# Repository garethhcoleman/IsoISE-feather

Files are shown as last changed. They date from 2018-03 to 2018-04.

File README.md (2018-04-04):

# IsoISE-feather
##Hardware files for IsoISE feather board

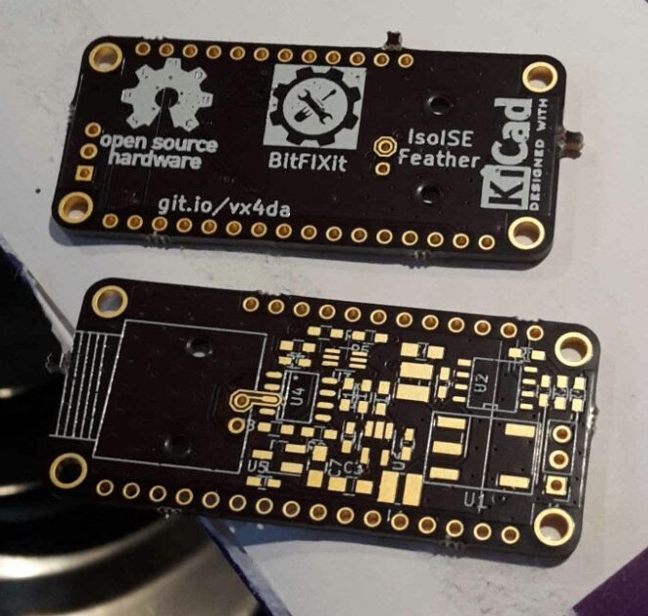
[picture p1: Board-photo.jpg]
Photo of IsoISE boards without components IsoISE boards without components

In this repo you will find all the design files; I hope it is everything you need to reproduce and hopefully improve my work.

This circuit is heavily based on wonderful work by Ryan Edwards at sparkyswidgets.com.

I emailed Ryan because I wanted to ask if he was happy for me to just make his isoion project, which is not strictly necessary but I think is good manners. He gave me his blessing to go ahead. I thought it was especially important to do this since he was selling his projects (although not this one, my orignal motivation for making it) and I wasn't then intending to modify his design. Subsequently I took the bull by the horns and dove into (partially!) understanding and modifying his designs, so I took his more advanced [ion selective electrode interface project](https://www.sparkyswidgets.com/portfolio-item/ion-selective-electrode-interface/) and went from there.

As you can see by comparing our circuits, I copied his design for the isolated I2C based ADC and digital pot, applied to a TL072 JFET op-amp front end. The only significant changes I made were to replace the isolated power supply and separate -5V generator with an isolated supply able to generate +-5V from 3.3V. I did this because the original ADUM6010 datasheet does not recommend the combination of VIN=3.3V and VOUT=5V.

The PCB layout is my own work, my first ever board produced and already I can see issues!! The guard rings around the signal input pin are very tightly spaced making soldering difficult - in a future revision I will increase the spacing there. I somehow ended up skipping the reference R3 - so there are 11 resistors on board numbered R1-R12. Again, I'll correct this in future revisions. I didn't pay much attention to silkscreen component references so assembly will require reference to the board layout in Kicad....

I'm following Dave Jones' OSHW logo and definition: https://www.eevblog.com/oshw/

S = Schematic - Included
P = PCB - Included
F = Firmware and/or software - TO BE DONE
M = Mechanical CAD files - NOT APPLICABLE
D = Design Documentation - This document
B = Bill Of Materials - Included
C = License used allows for commercial use - YES

I've used open software to produce these files: Kicad 4.0.7, LibreOffice 4.3 and Remarkable 1.87

You can order the revision 1 board at [OSH Park](https://oshpark.com/shared_projects/bHu0gW7W).
Additionally, a shared basket of almost all the required components is [available at digikey](http://www.digikey.co.uk/short/jpfbn8).

Licensed under the Creative Commons Attribution-ShareAlike 3.0 Unported license, following the license of the originating project.

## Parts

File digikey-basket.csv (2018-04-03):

Index | Quantity | Part Number | Description | Customer Reference | Available Quantity | Backorder Quantity | Unit Price GBP | Extended Price GBP
1 | 4 | 811-2374-ND | DC/DC CONVERT +/-5V 100MA 1W SMD | U1 | 4 | 0 | 5.39 | 21.56
2 | 4 | ADUM1250ARZ-ND | DGTL ISO 2.5KV 2CH I2C 8SOIC | U2 | 4 | 0 | 4.17 | 16.68
3 | 4 | MCP4017T-104E/LTCT-ND | IC DGTL POT 100K 128TAPS SC70-6 | U3 | 4 | 0 | 0.38 | 1.52
4 | 4 | 497-7040-1-ND | IC OPAMP JFET 4MHZ 8SO | U4 | 4 | 0 | 0.41 | 1.64
5 | 4 | 296-17098-1-ND | IC VREF SERIES 3V SOT23-3 | U5 | 4 | 0 | 1.93 | 7.72
6 | 4 | MCP3221A5T-I/OTCT-ND | IC ADC 12BIT 2.7V 1CH LP SOT23-5 | U6 | 4 | 0 | 1.05 | 4.2
7 | 20 | 399-15351-1-ND | CAP CER 0.1UF 6.3V X7R 0603 | C1,C2,C5,C6,C9 | 20 | 0 | 0.165 | 3.3
8 | 12 | 399-8014-1-ND | CAP CER 10UF 6.3V X5R 0805 | C3,C4,C7 | 12 | 0 | 0.126 | 1.51
9 | 4 | 399-15379-1-ND | CAP CER 220PF 10V X7R 0603 | C8 | 4 | 0 | 0.23 | 0.92
10 | 4 | ARF1065-ND | CONN BNC JACK R/A 50 OHM PCB | J2 | 4 | 0 | 2.82 | 11.28
11 | 8 | 811-2473-1-ND | FIXED IND 10UH 500MA 400 MOHM | L1,L2 | 8 | 0 | 0.23 | 1.84
12 | 12 | 541-4040-1-ND | RES SMD 3K OHM 1% 1/10W 0603 | R1,R2,R9 | 12 | 0 | 0.019 | 0.23
13 | 12 | 541-2201-1-ND | RES SMD 4.7K OHM 1% 1/10W 0603 | R4,R5,R6 | 12 | 0 | 0.056 | 0.67
14 | 4 | 311-10KDCT-ND | RES SMD 10K OHM 0.5% 1/10W 0603 | R7 | 4 | 0 | 0.08 | 0.32
15 | 8 | 311-2103-1-ND | RES SMD 100K OHM 0.5% 1/10W 0603 | R8,R10 | 8 | 0 | 0.11 | 0.88
16 | 4 | 311-1.0KDCT-ND | RES SMD 1K OHM 0.5% 1/10W 0603 | R11 | 4 | 0 | 0.08 | 0.32
17 | 4 | 311-499DCT-ND | RES SMD 499 OHM 0.5% 1/10W 0603 | R12 | 4 | 0 | 0.08 | 0.32

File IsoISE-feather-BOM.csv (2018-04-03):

Ref | Value | Part Ordered | Footprint | Datasheet
U1 | MTU1D0305MC | MTU1D0305MC | 5pinMTU | https://power.murata.com/data/power/ncl/kdc_mtu1.pdf
U2 | ADUM1250 | ADUM1250ARZ | SOIC-8-N | http://www.analog.com/media/en/technical-documentation/data-sheets/ADUM1250_1251.pdf
U3 | MCP4017 | MCP4017T-104E/LT | SOT-363_SC-70-6 | http://ww1.microchip.com/downloads/en/DeviceDoc/22147a.pdf
U4 | TL072 | TL072BIDT | SOP-8L | http://www.st.com/content/ccc/resource/technical/document/datasheet/bb/4d/19/24/7d/40/48/a6/CD00000490.pdf/files/CD00000490.pdf/jcr:content/translations/en.CD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
U5 | REF3130 | REF3130AIDBZT | SOT-23-3 | http://www.ti.com/lit/ds/symlink/ref3130.pdf
U6 | MCP3221 | MCP3221A5T-I/OT | SOT-23-5 | http://ww1.microchip.com/downloads/en/DeviceDoc/20001732E.pdf
C1 | 0.1uF | C0603C104K9RAC7867 | 603 | https://content.kemet.com/datasheets/KEM_C1002_X7R_SMD.pdf
C2 | 0.1uF | C0603C104K9RAC7867 | 603 | https://content.kemet.com/datasheets/KEM_C1002_X7R_SMD.pdf
C3 | 10uF | C0805C106M9PACTU | 805 | https://content.kemet.com/datasheets/KEM_C1002_X7R_SMD.pdf
C4 | 10uF | C0805C106M9PACTU | 805 | https://content.kemet.com/datasheets/KEM_C1002_X7R_SMD.pdf
C5 | 0.1uF | C0603C104K9RAC7867 | 603 | https://content.kemet.com/datasheets/KEM_C1002_X7R_SMD.pdf
C6 | 0.1uF | C0603C104K9RAC7867 | 603 | https://content.kemet.com/datasheets/KEM_C1002_X7R_SMD.pdf
C7 | 10uF | C0805C106M9PACTU | 805 | https://content.kemet.com/datasheets/KEM_C1002_X7R_SMD.pdf
C8 | 220pF | C0603C221K8RAC7867 | 603 | https://content.kemet.com/datasheets/KEM_C1002_X7R_SMD.pdf
C9 | 0.1uF | C0603C104K9RAC7867 | 603 | https://content.kemet.com/datasheets/KEM_C1002_X7R_SMD.pdf
J1 | Conn_01x03 | Standard pin header | 1x03_Pitch2.54mm
J2 | BNC | 31-5431 | BNC-Amphenol | https://www.amphenolrf.com/downloads/dl/file/id/7797/product/565/031_5431_10rfx_customer_drawing.pdf
J3 | FeatherWing | OshPARK
L1 | 10uH | 82103C | Murata_8200 | https://www.murata-ps.com/data/magnetics/kmp_8200c.pdf
L2 | 10uH | 82103C | Murata_8200 | https://www.murata-ps.com/data/magnetics/kmp_8200c.pdf
R1 | 3K | CRCW06033K00FKEAC | 603
R2 | 3K | CRCW06033K00FKEAC | 603
R4 | 4.7K | RCA06034K70FKEA | 603
R5 | 4.7K | RCA06034K70FKEA | 603
R6 | 4.7K | RCA06034K70FKEA | 603
R7 | 10K | RT0603DRD0710KL | 603
R8 | 100K | AT0603DRD07100KL | 603
R9 | 3K | CRCW06033K00FKEAC | 603
R10 | 100K | AT0603DRD07100KL | 603
R11 | 1K | RT0603DRD071KL | 603
R12 | 500R | RT0603DRD07499RL | 603

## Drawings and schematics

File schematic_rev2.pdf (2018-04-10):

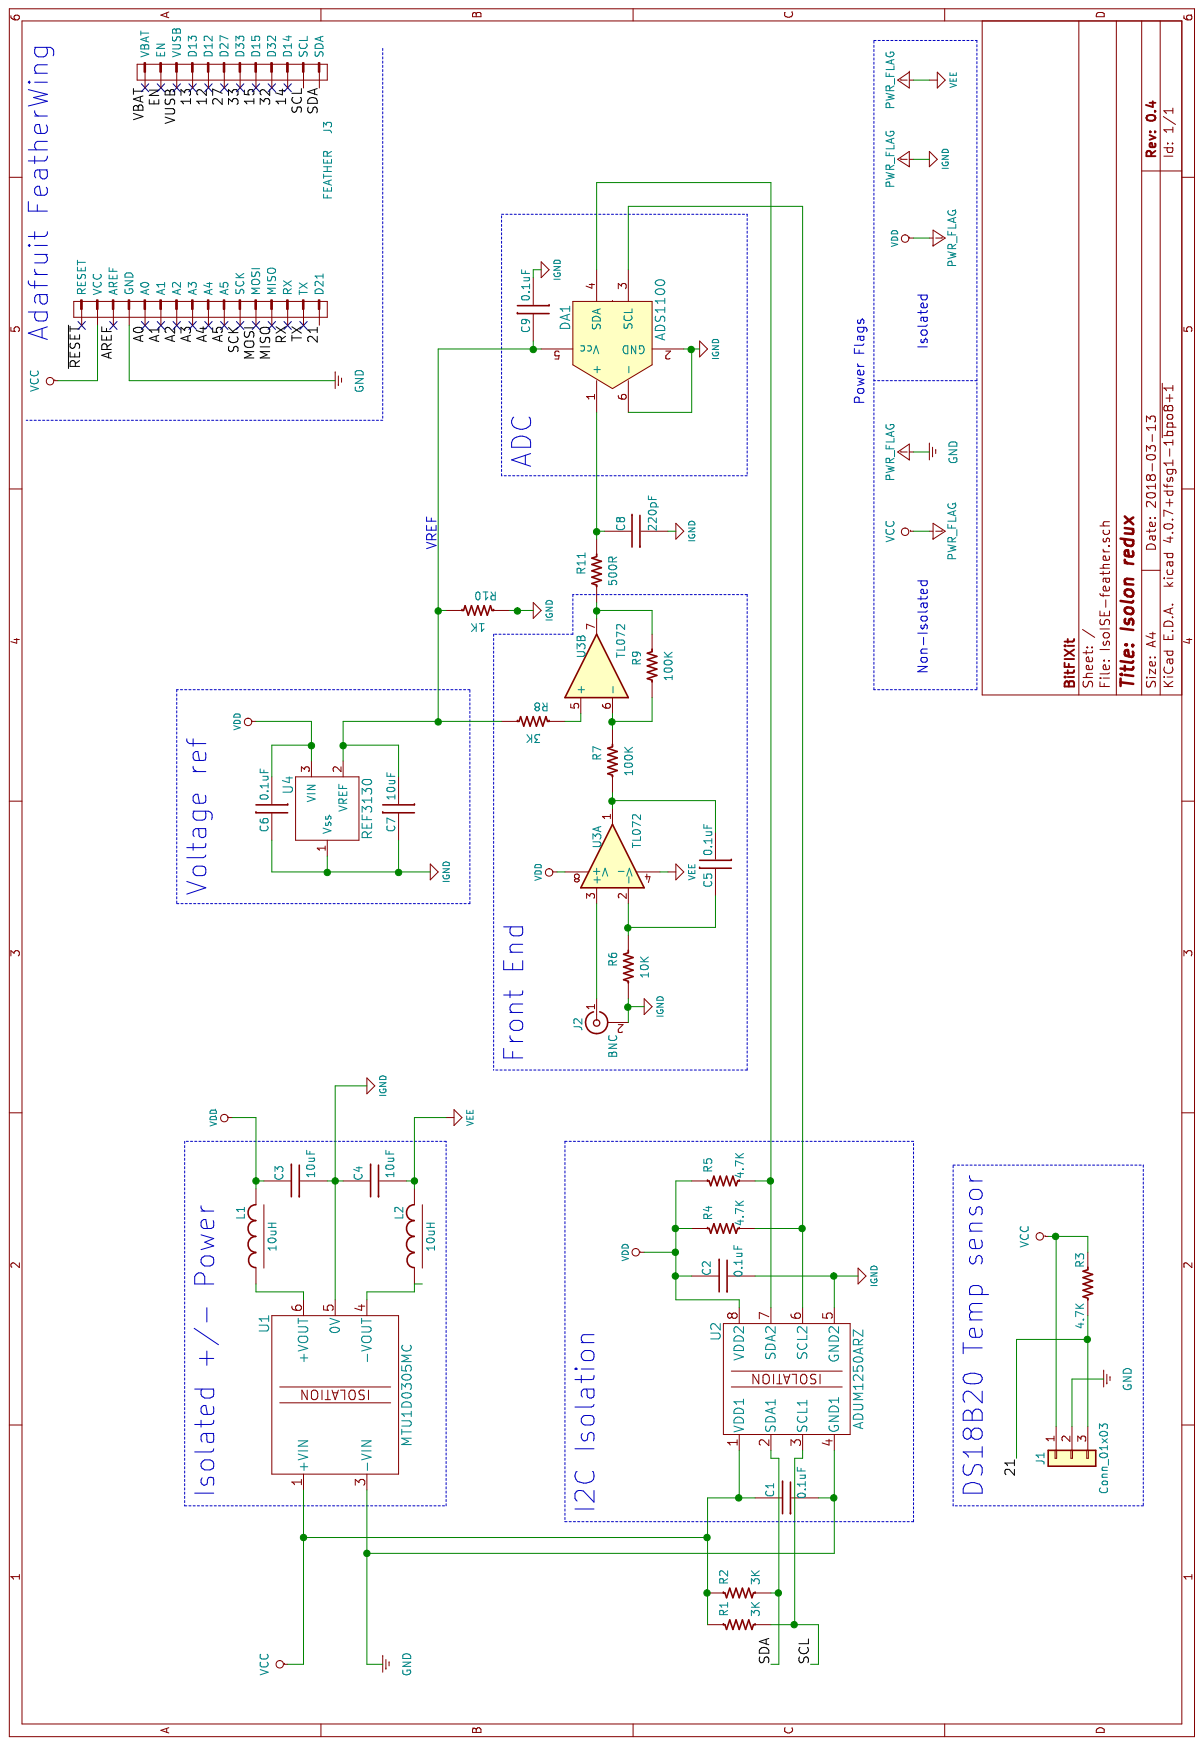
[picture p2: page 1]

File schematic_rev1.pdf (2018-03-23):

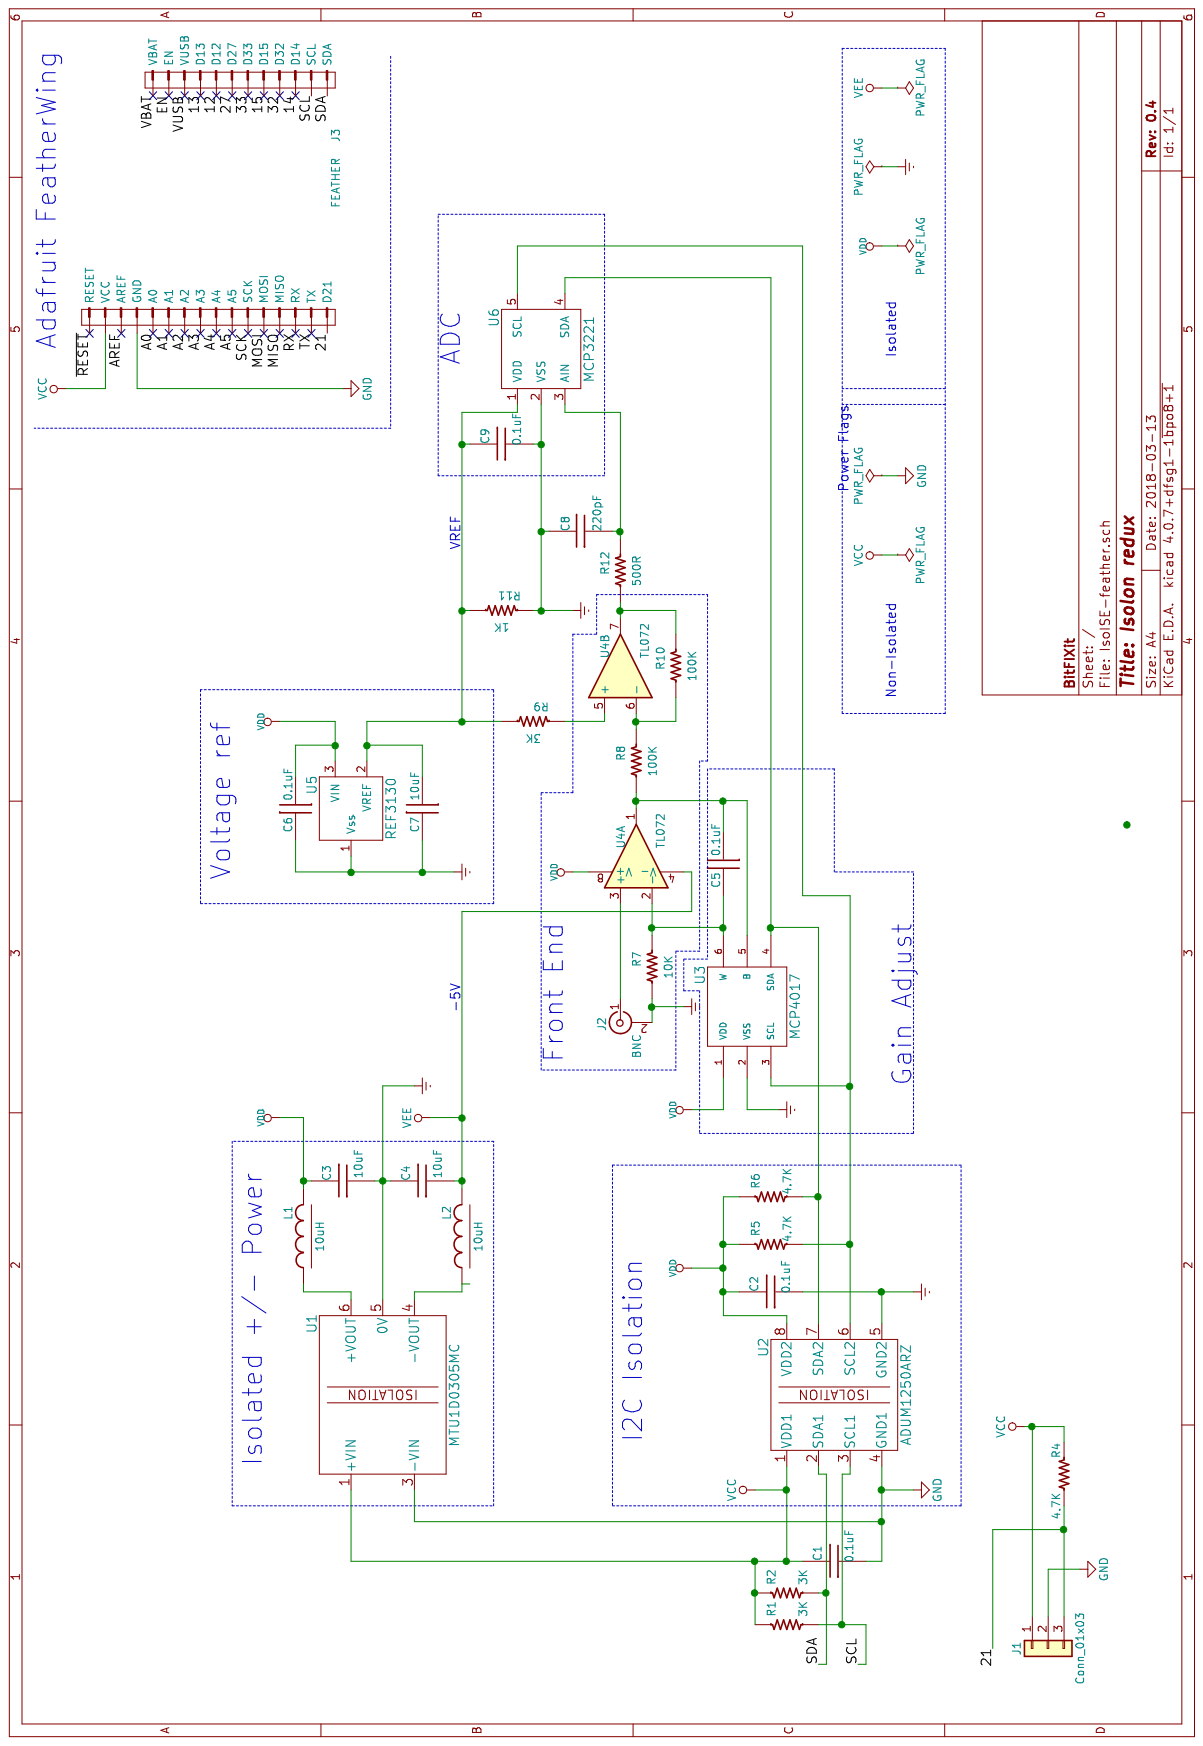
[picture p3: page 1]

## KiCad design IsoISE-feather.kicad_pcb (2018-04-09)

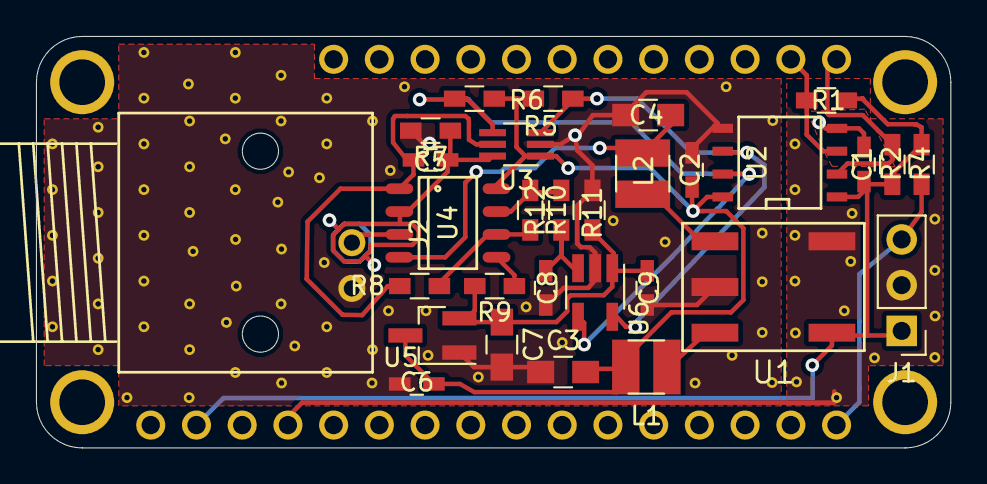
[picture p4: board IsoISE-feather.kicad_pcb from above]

Board: 2 copper layers, 50.8 x 22.9 mm, 31 parts (0 on the bottom side), 20 nets.

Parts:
C1, C2, C5, C6, C9: 0.1uF; C_0603_HandSoldering
C3, C4, C7: 10uF; C_0805_HandSoldering
C8: 220pF; C_0603_HandSoldering
J1: Conn_01x03; Pin_Header_Straight_1x03_Pitch2.54mm
J2: BNC; BNC_Socket_Gmod
J3: FEATHER; FeatherWing
L1, L2: 10uH; Inductor_Murata_8200
R1, R2, R9: 3K; R_0603_HandSoldering
R4, R5, R6: 4.7K; R_0603_HandSoldering
R7: 10K; R_0603_HandSoldering
R8, R10: 100K; R_0603_HandSoldering
R11: 1K; R_0603_HandSoldering
R12: 500R; R_0603_HandSoldering
U1: MTU1D0305MC; 5pinMTU
U2: ADUM1250ARZ; SOIC-8-N
U3: MCP4017; SOT-363_SC-70-6_Handsoldering
U4: TL072; SOP-8L
U5: REF3130; SOT-23_Handsoldering
U6: MCP3221; SOT-23-5_HandSoldering

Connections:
/21: J1.3, J3.16, R4.2
/SCL: J3.27, R1.2, U2.3
/SDA: J3.28, R2.2, U2.2
Earth: C2.1, C3.1, C4.2, C6.2, C7.2, C8.1, C9.1, J2.2, R7.2, R11.1, U1.5, U2.5, U3.2, U5.1, U6.2
GND: C1.1, J1.2, J3.4, U1.3, U2.4
unnamed: C5.1, R8.2, U3.5, U4.1
unnamed: C5.2, R7.1, U3.6, U4.2
unnamed: C7.1, C9.2, R9.2, R11.2, U5.2, U6.1
unnamed: C8.2, R12.1, U6.3
unnamed: J2.1, U4.3
unnamed: L1.1, U1.6
unnamed: L2.1, U1.4
unnamed: R5.2, U2.6, U3.3, U6.5
unnamed: R6.2, U2.7, U3.4, U6.4
unnamed: R9.1, U4.5
unnamed: R10.1, R12.2, U4.7
unnamed: R8.1, R10.2, U4.6
VCC: C1.2, J1.1, J3.2, R1.1, R2.1, R4.1, U1.1, U2.1
VDD: C2.2, C3.2, C6.1, L1.2, R5.1, R6.1, U2.8, U3.1, U4.8, U5.3
VEE: C4.1, L2.2, U4.4

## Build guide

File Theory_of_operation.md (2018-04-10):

# IsoISE-feather
## Theory of operation

The name IsoISE refers to the main purpose of this board - a fully electrically isolated Ion Selective Electrode (ISE) meter. ISE probes are available to measure the concentration of a range of ions in solution. The most common ISE probe is a pH probe, but probes are available for a range of other ions such as nitrate, ammonia etc. This circuit gives an I^2^C reading corresponding to the voltage of the probe, with variable gain between 1-8x. It also features a connection for a waterproof temperature probe.

The IsoISE-feather uses the feather form factor developed by Lady Ada at [Adafruit](https://www.adafruit.com/) ; they are amazing; they just keep on cranking out great products backed up with libraries, tutorials, etc. Please support them so they can continue their great work. Using the feather format means that the microcontroller can be supplied by the user, together with lcd, buttons etc if desired.

This circuit is based on wonderful work by Ryan Edwards at [sparkyswidgets.com](http://www.sparkyswidgets.com/). Rev1 was heavily based on his original work, with rev 2 I've changed most of the components in an attempt to simplify the circuit and improve accuracy.

 A block diagram of the circuit is given here for reference:

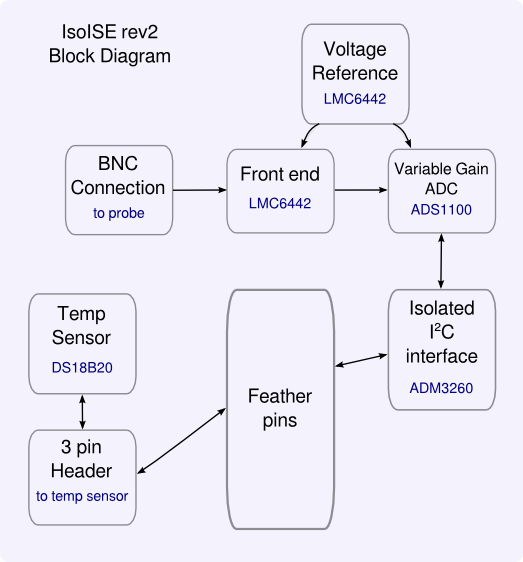
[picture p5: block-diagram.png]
IsoISE block diagram


The input signal from the probe arrives at the front end, which is a pair of ultra-low input bias current op-amps.

The signal is passed onto the ADC, which is 16-bit, has programmable gain of 1-8x and features self calibration from the supply voltage. We are using a precision voltage reference to power the ADC as well as provide a reference to the front end.

A digitised value from the ADC is read by the microcontroller across the isolated I^2^C interface. The interface also provides isolated power for the voltage reference and op-amps.

Additionally, a pin header is supplied to allow the connection of a waterproof temperature sensor, the DS18B20. It is widely available and accurate to >0.1&deg;C.

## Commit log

2018-03-23 added first draft of kicad files
    [IsoISE-feather.kicad_pcb, IsoISE-feather.sch]
2018-03-23 tweaked silkscreen and replaced bnc to get 3d model..
    [IsoISE-feather.kicad_pcb]
2018-04-03 files as submitted to oshpark
    [IsoISE-feather.kicad_pcb]
2018-04-03 added seperate BOM as .csv
    [IsoISE-feather-BOM.csv]
2018-04-03 added real part numbers to BOM and digikey basket
    [IsoISE-feather-BOM.csv, digikey-basket.csv]
2018-04-09 updated logo on board
    [IsoISE-feather.kicad_pcb]
